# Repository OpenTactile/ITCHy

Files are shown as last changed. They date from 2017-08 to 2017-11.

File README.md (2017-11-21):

# ITCHy
The *Interactive Tactile display Control Handle*

ITCHy is a combined input/output device similar to a conventional computer mouse. It provides accurate tracking of absolute position, orientation as well as translational and angular velocities - thanks to its *two* ADNS9800 laser sensors. Using a total of 20 vibrating actuators, various tactile impressions can be transmitted to ones fingertip. Additional buttons and a RGB LED allows for basic user interaction.

ITCHy is intended to be used in conjunction with the [SCRATCHy system](https://github.com/OpenTactile/SCRATCHy).<br>
However, it can also be used in a stand-alone fashion.

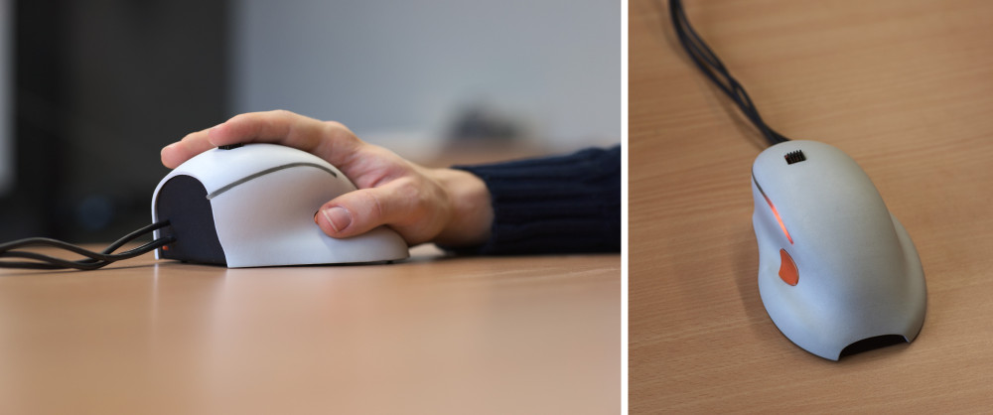
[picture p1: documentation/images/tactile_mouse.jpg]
Image of the tactile mouse


### Parts needed for building the Tactile Mouse

Positional und rotational tracking is done using two *ADSN9800 Motion Sensor* boards, both connected to a *PJRC Teensy 3.2* USB Development Board via [SPI](https://en.wikipedia.org/wiki/Serial_Peripheral_Interface_Bus). By adding some buttons and a RGB LED (optional), additional user interaction is possible.

  * Teensy 3.2 USB Development Board<br>
    see, e.g. https://www.pjrc.com/store/teensy32.html    
  * Two ADNS 9800 Laser Motion Sensors<br>
    https://www.tindie.com/products/jkicklighter/adns-9800-laser-motion-sensor/
  * Flexible USB-A to Micro-USB cable of appropriate length  
  * Microswitch (as used in computer mice, e.g. [this one](http://www.newark.com/omron-electronic-components/d2f/microswitch-pin-plunger-spdt-3a/dp/36K7257)) for the thumb button
  * Tactile switch for the reset button (e.g. [this one](http://www.newark.com/alps/skhhaqa010/switch-tactile-6x6mm-vert-red/dp/94T3234))
  * (optional) RGB LED or 3 individual LEDs
  * (optional) Appropriate resistors for operating the LEDs
  
3D printable parts are located in the *tactileMouse* subfolder. For convenience, single parts have been exported to *stl* Format that should be appropriate for most manufacturers. If modifications are needed, please use [Blender](https://www.blender.org/) for editing the *tactileMouse.blend* file.

We have positive experiences with [Shapeways](https://www.shapeways.com/) for manufacturing the parts using the following materials:

  * mouse_base.stl &rarr; [Strong & Flexible Plastic](https://www.shapeways.com/materials/strong-and-flexible-plastic), Black
  * mouse_buttons.stl &rarr; [Strong & Flexible Plastic](https://www.shapeways.com/materials/strong-and-flexible-plastic), Orange Polished
  * mouse_cover.stl &rarr; [Strong & Flexible Plastic](https://www.shapeways.com/materials/strong-and-flexible-plastic), White Polished
  * mouse_diffusor.stl &rarr; [Acrylic Plastic](https://www.shapeways.com/materials/acrylic-plastic), Transparent Acrylic (Transparent Detail)

***Important: Always check dimensions of individual parts before printing!***

### Parts needed for building the tactile display

Similar to the Tactile Mouse, parts for 3D printing the tactile display are located in the folder *tactileDisplay*. Depending on the PZT actuators to be used, modifications may have to be done to the "spacer" part within the *tactileDisplay.blend* file.

If the parts are printed using Shapeways, the following materials are appropriate:

  * base.stl &rarr; [Strong & Flexible Plastic](https://www.shapeways.com/materials/strong-and-flexible-plastic), e.g. Blue Polished
  * holder.stl (optional part, not needed for operation)
  * press_merged.stl &rarr; [Steel](https://www.shapeways.com/materials/steel), e.g. Polished Nickel<br>
    To save money, both halves of the press have been merged into a single part. Please separate (and clean) the parts manually.
  * spacer.stl &rarr; [Frosted Ultra Detail](https://www.shapeways.com/materials/frosted-detail-plastic)<br>
    *Be careful, the small springs are extremely brittle!*
  * top.stl &rarr; [Strong & Flexible Plastic](https://www.shapeways.com/materials/strong-and-flexible-plastic), e.g. White Polished
  
Additional parts needed:
  * 4x Cylinderhead screw, M2.5 x 30mm
  * 4x M2.5 nut
  * Cable for connecting the actuators<br>(depending of the chosen actuator configuration, choose as flexible and light as possible)

Please have a look into the *tactileDisplay.blend* file to get an idea on how to put the parts together.

**Hint:** Applying some electrical isolation (e.g. some layers of enamel) on the top of the actuators is generally a good idea. Otherwise the driving voltage may come into direct contact with the fingertip!

This is how it should look like after assembling the parts:
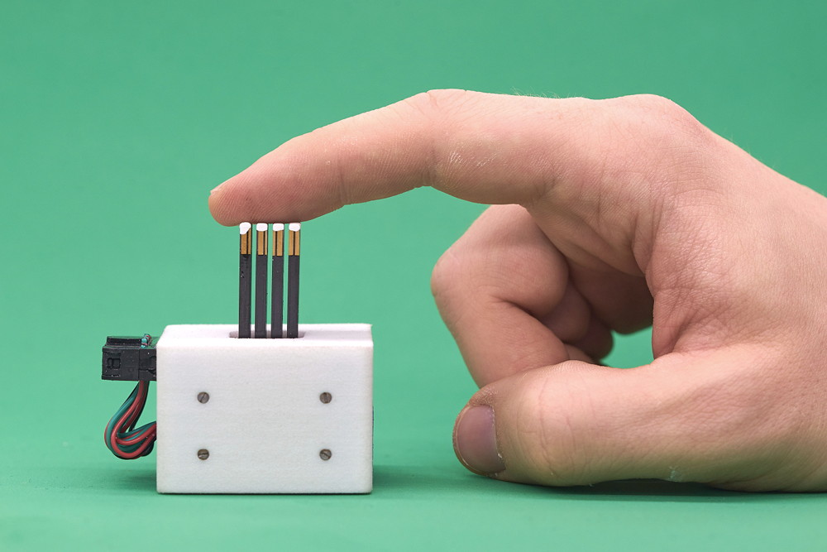
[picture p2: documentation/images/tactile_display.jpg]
Image of the tactile display


### Building libITCHy
libITCHy uses the qmake build system and is available for linux platforms only. For building and installing the library system-wide, please follow these steps within the base directory:

```shell
mkdir libITCHy-build
cd libITCHy-build
qmake ../libITCHy
make && make install
```

### Building and flashing the firmware
Before the Teensy can be flashed, please install Teensyduino by following the [official instructions](https://www.pjrc.com/teensy/td_download.html). Afterwards, building and flashing the firmware is straightforward:

```shell
cd teensyHIDSimulator
make
```
If the build process was successfull, you can install the firmware by connecting the Teensy (or better say the whole Tactile Mouse) via USB and running

```shell
make upload
```
Afterwards, the RGB LED of the mouse should blink shortly in a orangish color after connecting it to USB.

### Calibrating and testing the sensors
After libITCHy has been installed, the sensors can be tested using the *ITCHyCalibration* application:

```shell
mkdir ITCHyCalibration-build
cd ITCHyCalibration-build
qmake ../ITCHyCalibration
make
./ITCHyCalibration
```

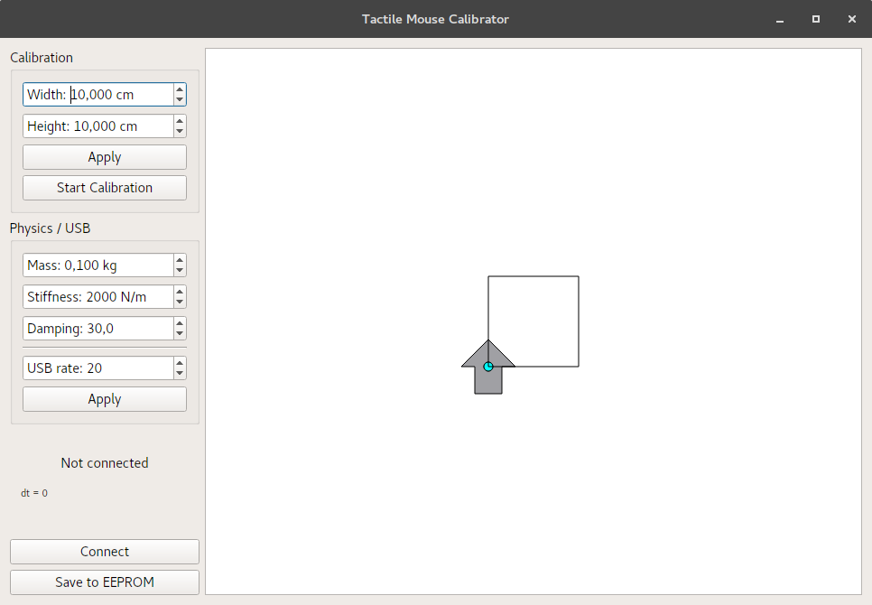
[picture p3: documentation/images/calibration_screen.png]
The calibration application


After connecting the tactile mouse and by pressing the *Connect* button, the status area on the left should show "Connected" and the current simulation timestep should be displayed.

##### Calibration procedure
When connecting the tactile mouse for the first time, a calibration of the sensors is needed. Please follow this procedure for proper calibration:
1. Use a (probably quite large) hard-plastic mousepad
2. Mark a distance of e.g. 10cm (or larger depending on the dimensions of the mousepad) in horizontal direction as well as in vertical direction
3. Register these distance within the GUI and click *Apply*
4. Place the tactile mouse in the bottom left of the calibration area
5. Click *Start Calibration*
6. Steadily move the device across the horizontal marker
7. Press the thumb button
8. Steadily move the device across the vertical marker
9. Press the thumb button again

After this procedure is finished, moving the mouse should show a corresponding reaction of the "arrow" in the window. You can reset orientation and position to defaults at any time by pressing the small button at the front of the device.

The ADNS sensors seem to be quite picky regarding the surface properties of the mousepad. In case no proper calibration is possible, please try another one. We made good experiences with the [Corsair MM400](http://www.corsair.com/en-ww/mm400-high-speed-gaming-mouse-pad) mousepad.

In order to save the new calibration data permanently, press the *Save to EEPROM* button.

##### Parameter tuning
The firmware inside the tactile mouse use a simple physics simulation that models the virtual representation of itself as a rigid body attached to the actual sensor position via two springs. The parameters shown in the GUI allow to adjust the simulation parameters such as:
- The mass of the rigid body,
- the stiffness of the springs and
- a damping factor for suppressing oscillations

After changing the values and hitting *Apply* the changes are visible immediately. Again, they will be store permanently after the *Save to EEPROM* button has been pressed.

By adjusting the *USB rate* of the tactile mouse, one can limit the polling rate of the device. This value can be decreased down to 1ms, resulting in a maximum polling rate of 1000Hz. Please note, however, that this may increase the load of the host system (and the kernel actually has to support such high polling rates).

### Using libITCHy
Using libITCHy directly (without SCRATCHy) is straightforward, as can be seen in this minimal example program:
```cpp
#include <itchy.h>
#include <cmath>

int main(int argc, char *argv[]) {
    ITCHy mouse;
    mouse.connect(); // Wait until the mouse gets connected
    
    // This variable will hold the last valid state
    // e.g. velocity, position, etc.
    ITCHy::State state = mouse.currentState(); 

    while(state.button == 0) { // Loop until a button on the mouse gets pressed
        state = mouse.currentState(); // Update state via USB
        
        // Change the internal RGB LED
        mouse.setColor({uint8_t(255 * 10 * state.velocity[0]),
                        uint8_t(255 * 10 * state.velocity[1]),
                        uint8_t(255 * state.angle / (2 * M_PI))});
    }

    mouse.disconnect();
    return 0;
}
```
This example program should be pretty self-explanatory.
Compiling and running this application can be done as follows:
```shell
g++ -o itchyMinimal minimal.cpp -I/usr/include/itchy/ -lITCHy
./itchyMinimal
```
When moving the tactile mouse, the RGB LED now should change colors according to the current speed and orientation of the device.

### Using the Python bindings
If you prefer to access the Tactile Mouse using Python, the ITCHPy library can be build as follows:

```shell
cd ITCHPy
make
```

To test if all dependencies are met and the whole build process was successful run
```shell
python itchpytest.py
```
within the same directory.

This file also gives some hints on how to include ITCHPy in your projects.

## API Reference

#### ICTHy
This class allows to communicate with the hardware device directly (without the need for libSCRATCHy).

The default constructor assumes that the Teensy 3.2 that is used within the mouse can be identified using the ID `{0x16C0, 0x0486, 0xFFAB, 0x0200}`. 
In case this default has been changed, the ID to connect to can be specified manually by calling `ITCHy({0x????, 0x????, 0x????, 0x????})`

##### `void connect()`
Tries to connect to the device via USB periodically. Will return after ITCHy has been successfully initialized. (Blocking operation)

After successfull initialization, the `Connected` callback will be executed.

##### `bool tryConnect()`
Tries to connect to the device via USB *once*. Returns `true` if the devices has been initialized successfully or `false` if the device has not been found.

After successfull initialization, the `Connected` callback will be executed.

##### `void disconnect()`
Closes the USB device handle and executes the `Disconnected` callback afterwards.

##### `bool connected() const`
Returns whether the USB devices has been successfully initialized or not.

##### `bool setCalibrationParameters(const vec2f& target)`
Sets the dimensions of the calibration area in metres. Using the *ITCHyCalibration* application is the recommended way to alter this value.

Returns `false` if the device is not connected or a USB communication error occured.

##### `bool setSimulationParameters(float mass, float stiffness, float damping, int updateRate)`
Sets the internal simulation parameters of the tactile mouse and causes these values to be used immediately.

In case instabilities occur due to wrong parameters, a total reset of the device is needed!
Using the *ITCHyCalibration* application is the recommended way to alter this value.

Returns `false` if the device is not connected or a USB communication error occured.

##### `bool setColor(const color& cl)`
Changes the color of the built in RGB LED. Color values are specified within 0...255 range. 

For example
```cpp
setColor({255, 128, 0})
```
will cause the LED to emit an orange color, while
```cpp
setColor({0, 0, 0})
```
will turn off the LED.

Returns `false` if the device is not connected or a USB communication error occured.

##### `bool startCalibration()`
Initiates the calibration process as has been discussed in section *Calibration procedure*.

Returns `false` if the device is not connected or a USB communication error occured.

##### `bool saveState()`
Stores the current configuration to the internal EEPROM, causing these settings to be loaded automatically after connecting.

This method will store the following data:

- Size of calibration area
- Calibration matrix for both sensors
- Simulation parameters (mass, stiffness, damping and USB update rate)

Returns `false` if the device is not connected or a USB communication error occured.

##### `const State& currentState(unsigned int timeout = 50)`
Tries to acquire the latest state of the tactile mouse via USB, waiting a maximum of `timeout` milliseconds for the device to react. In case no new data is available or a timeout occured, the last valid state will be returned. 

The returned struct should be self-explanatory:
```cpp
struct State {
  // Actual output (25 bytes)
  vec2f position;
  float angle;
  vec2f velocity;
  float angularVelocity;
  byte  button;

  // Raw sensor data (16 bytes)
  vec2f leftSensor; // equals std::array<float, 2>
  vec2f rightSensor; // equals std::array<float, 2>

  // Debug data (8 bytes)
  vec2s leftIncrement;    // Contains sensor delta since last USB frame, equals std::array<int16_t, 2>
  vec2s rightIncrement;   // Contains sensor delta since last USB frame, equals std::array<int16_t, 2>

  // Simulation info (8 bytes)
  float timeStep;
  float time;

  // Unused
  byte unused[7];
};
```
In case a USB communication error occured, the device will be disconnected and the `CommunicationError` callback will be executed.

##### `void addCallback(CallbackType type, const std::function<void()>& callback)`
Allows to register a custom function that will be called if the corresponsing event happens. 

Multiple functions can be added. However, removing them afterwards is currently not supported.

The following example will print an error message in case USB communication failed:
```cpp
  itchyinstance.addCallback(
    ITCHy::CallbackType::CommunicationError, 
    [](){ // Add lambda function
      std:cout << "USB error" << std::endl;
    });
```

#### TactileMouseQuery
This class implements the `PositionQuery` defined in libSCRATCHy. Please refer to the [interface documentation](https://github.com/OpenTactile/SCRATCHy#positionquery) for further details.
ITCHy supports all of the `PositionQuery` calls, such as retrieval of position, orientation, velocity, angular velocity and status of the thumb button. Using the `feedback` method, the colour of the integrated LED can be changed freely.

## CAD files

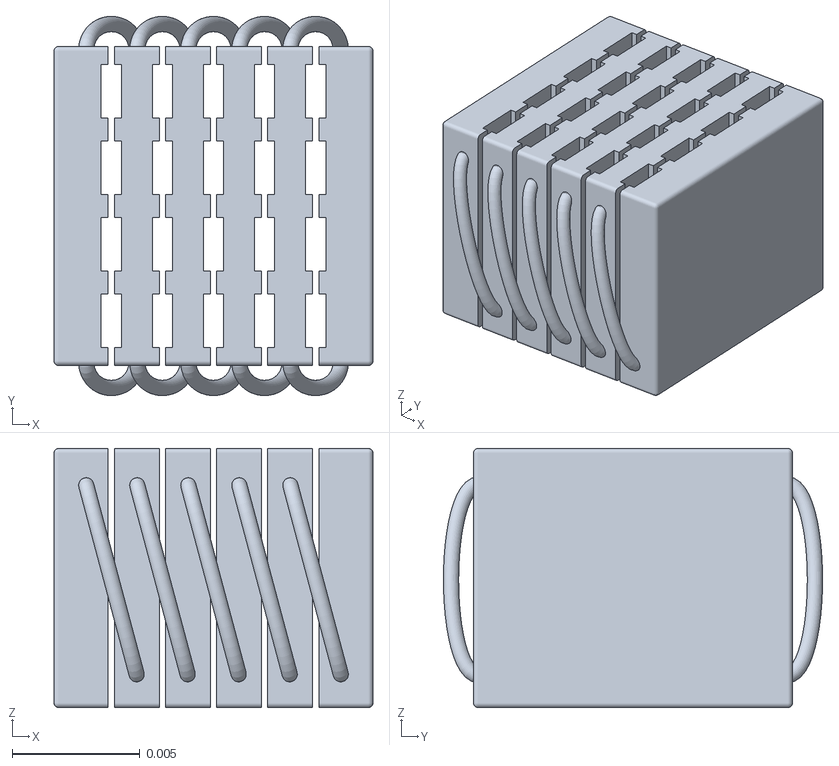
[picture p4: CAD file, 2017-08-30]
tactileDisplay/parts/spacer.stl
0.0125 x 0.0149 x 0.0101

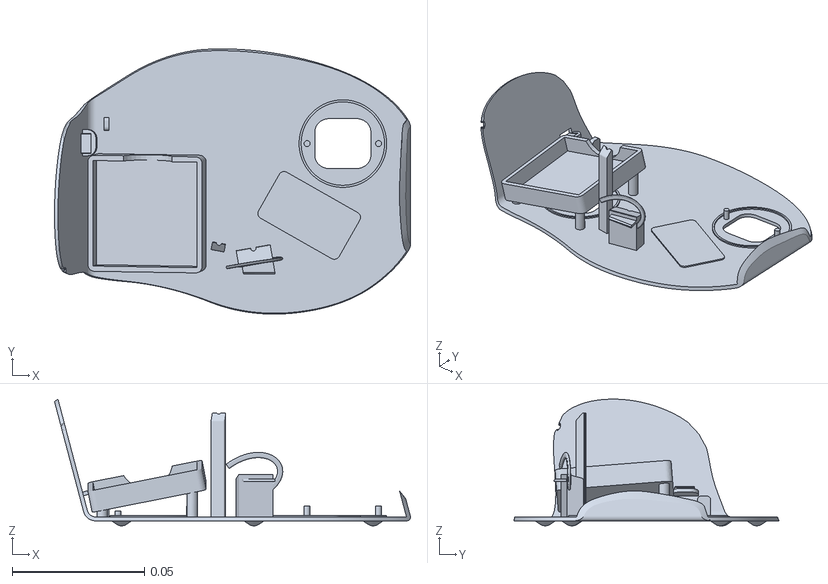
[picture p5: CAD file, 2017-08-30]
tactileMouse/parts/mouse_base.stl
0.134 x 0.1 x 0.0479

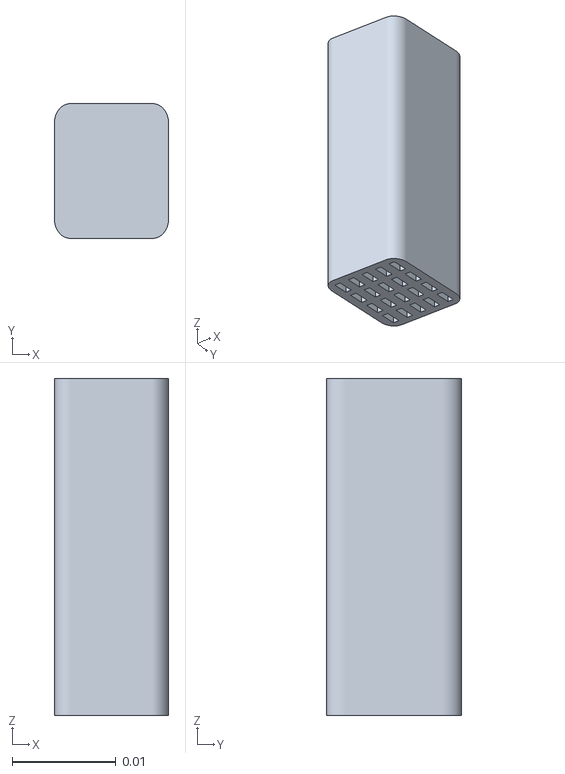
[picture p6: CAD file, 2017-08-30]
tactileDisplay/parts/holder.stl
0.011 x 0.013 x 0.0325

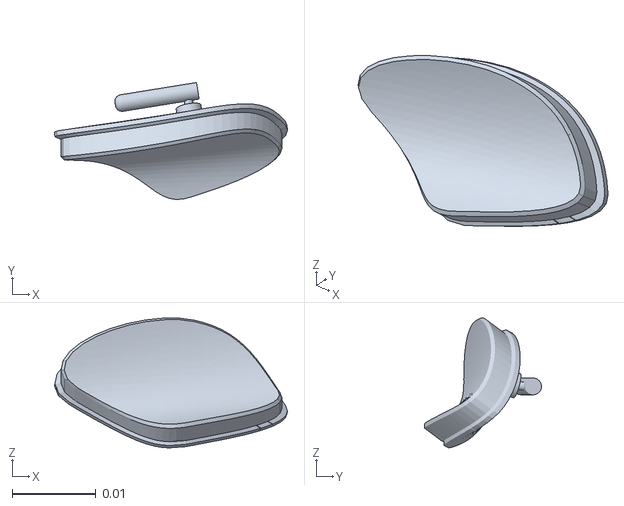
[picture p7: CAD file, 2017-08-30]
tactileMouse/parts/mouse_buttons.stl
0.0278 x 0.014 x 0.0155

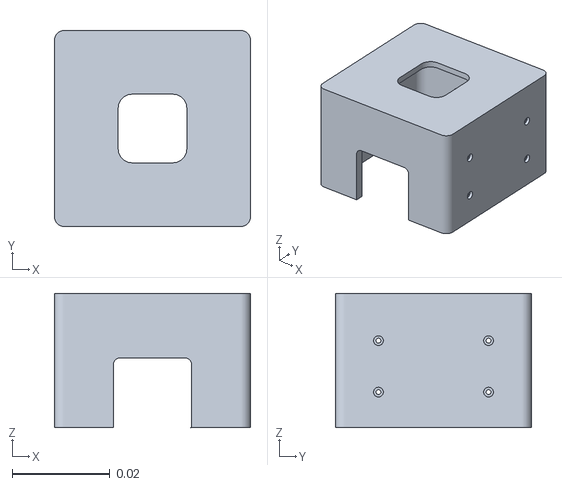
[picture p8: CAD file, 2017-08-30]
tactileDisplay/parts/top.stl
0.04 x 0.04 x 0.0274

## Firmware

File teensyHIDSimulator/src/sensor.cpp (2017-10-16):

#include "sensor.h"

#include <WProgram.h>
#include <avr/pgmspace.h>
#include "../firmware/adns9800_srom_A6.h"
#include "statusled.h"
#include <SPI.h>

// Registers
#define REG_Product_ID                           0x00
#define REG_Revision_ID                          0x01
#define REG_Motion                               0x02
#define REG_Delta_X_L                            0x03
#define REG_Delta_X_H                            0x04
#define REG_Delta_Y_L                            0x05
#define REG_Delta_Y_H                            0x06
#define REG_SQUAL                                0x07
#define REG_Pixel_Sum                            0x08
#define REG_Maximum_Pixel                        0x09
#define REG_Minimum_Pixel                        0x0a
#define REG_Shutter_Lower                        0x0b
#define REG_Shutter_Upper                        0x0c
#define REG_Frame_Period_Lower                   0x0d
#define REG_Frame_Period_Upper                   0x0e
#define REG_Configuration_I                      0x0f
#define REG_Configuration_II                     0x10
#define REG_Frame_Capture                        0x12
#define REG_SROM_Enable                          0x13
#define REG_Run_Downshift                        0x14
#define REG_Rest1_Rate                           0x15
#define REG_Rest1_Downshift                      0x16
#define REG_Rest2_Rate                           0x17
#define REG_Rest2_Downshift                      0x18
#define REG_Rest3_Rate                           0x19
#define REG_Frame_Period_Max_Bound_Lower         0x1a
#define REG_Frame_Period_Max_Bound_Upper         0x1b
#define REG_Frame_Period_Min_Bound_Lower         0x1c
#define REG_Frame_Period_Min_Bound_Upper         0x1d
#define REG_Shutter_Max_Bound_Lower              0x1e
#define REG_Shutter_Max_Bound_Upper              0x1f
#define REG_LASER_CTRL0                          0x20
#define REG_Observation                          0x24
#define REG_Data_Out_Lower                       0x25
#define REG_Data_Out_Upper                       0x26
#define REG_SROM_ID                              0x2a
#define REG_Lift_Detection_Thr                   0x2e
#define REG_Configuration_V                      0x2f
#define REG_Configuration_IV                     0x39
#define REG_Power_Up_Reset                       0x3a
#define REG_Shutdown                             0x3b
#define REG_Inverse_Product_ID                   0x3f
#define REG_Motion_Burst                         0x50
#define REG_SROM_Load_Burst                      0x62
#define REG_Pixel_Burst                          0x64

Sensor::Sensor(std::array<unsigned char, 2> pins, bool flipX, bool flipY)
{
    this->lifted = false;
    this->flipX = flipX;
    this->flipY = flipY;
    integrated = {{0,0}};
    this->pins = pins;
    pinMode (pins[0], OUTPUT); // Chip select
    pinMode (pins[1], INPUT_PULLUP); // Motion pin
    //attachInterrupt(mot, sensorChanged, FALLING);

    // TODO: which parts of the code have to be executed once / foreach sensor ?
    adns_com_end(); // ensure that the serial port is reset
    adns_com_begin(); // ensure that the serial port is reset
    adns_com_end(); // ensure that the serial port is reset
    adns_write_reg(REG_Power_Up_Reset, 0x5a); // force reset
    delay(50); // wait for it to reboot
    // read registers 0x02 to 0x06 (and discard the data)
    adns_read_reg(REG_Motion);
    adns_read_reg(REG_Delta_X_L);
    adns_read_reg(REG_Delta_X_H);
    adns_read_reg(REG_Delta_Y_L);
    adns_read_reg(REG_Delta_Y_H);
    // upload the firmware
    uploadFirmware();

    delay(10);
    //enable laser(bit 0 = 0b), in normal mode (bits 3,2,1 = 000b)
    // reading the actual value of the register is important because the real
    // default value is different from what is said in the datasheet, and if you
    // change the reserved bytes (like by writing 0x00...) it would not work.
    byte laser_ctrl0 = adns_read_reg(REG_LASER_CTRL0);
    adns_write_reg(REG_LASER_CTRL0, laser_ctrl0 & 0xf0 );
    //adns_write_reg(REG_Configuration_I, 0x01 ); // 200 dpi
    //adns_write_reg(REG_Configuration_I, 0x09 ); // 1800 dpi
    //adns_write_reg(REG_Configuration_I, 0x29 ); // 8200 dpi
    adns_write_reg(REG_Configuration_I, 0xA4 ); // 8200 dpi

    delay(1);
}

void Sensor::setCalibrationTarget(vec2f target)
{
    calibrationTarget = target;
}

void Sensor::adns_com_begin()
{
    digitalWrite(pins[0], LOW);
}

void Sensor::adns_com_end()
{
    digitalWrite(pins[0], HIGH);
}

byte Sensor::adns_read_reg(byte reg_addr)
{
    adns_com_begin();    
    SPI.transfer(reg_addr & 0x7f );
    delayMicroseconds(100);
    byte data = SPI.transfer(0);
    delayMicroseconds(1);
    adns_com_end();
    delayMicroseconds(19);
    return data;
}

void Sensor::adns_write_reg(byte reg_addr, byte data)
{
    adns_com_begin();    
    SPI.transfer(reg_addr | 0x80 );
    SPI.transfer(data);
    delayMicroseconds(20);
    adns_com_end();
    delayMicroseconds(100);
}

void Sensor::uploadFirmware()
{    
    adns_write_reg(REG_Configuration_IV, 0x02);
    adns_write_reg(REG_SROM_Enable, 0x1d);
    delay(10);
    adns_write_reg(REG_SROM_Enable, 0x18);
    adns_com_begin();
    SPI.transfer(REG_SROM_Load_Burst | 0x80);
    delayMicroseconds(15);
    unsigned char c;
    for (int i = 0; i < firmware_length; i++) {
      c = (unsigned char)pgm_read_byte(firmware_data + i);
      SPI.transfer(c);
      delayMicroseconds(15);
    }
    adns_com_end();
}

vec2f Sensor::integrate()
{
    vec2f delta = {{0.0f, 0.0f}};
    short deltaX = 0;
    short deltaY = 0;

    byte motion = adns_read_reg(REG_Motion);

    // semantic see datasheet
    bool motionOccured = motion & 0x80;
    bool motionFault = motion & 0x40;
    bool laserValid = motion & 0x20;

    byte SQUAL = adns_read_reg(REG_SQUAL);
    lifted = (SQUAL < 50);

    if(motionOccured && !motionFault && laserValid)
    {
        deltaX = (short) adns_read_reg(REG_Delta_X_L) |
                    ((short) adns_read_reg(REG_Delta_X_H) << 8);
        deltaY = (short) adns_read_reg(REG_Delta_Y_L) |
                    ((short) adns_read_reg(REG_Delta_Y_H) << 8);
    }

    if(!laserValid)
    {
        StatusLED::instance().blink({{255,0,0}}, 1.0);
        StatusLED::instance().blink({{255,128,0}}, 0.5);
    }

    if(motionFault)
    {
        StatusLED::instance().blink({{255,0,0}}, 1.0);
        StatusLED::instance().blink({{255,128,0}}, 0.5);
        StatusLED::instance().blink({{255,128,0}}, 0.5);
    }

    if(flipX)
        deltaX *= -1;
    if(flipY)
        deltaY *= -1;

    integrated[0] += deltaX;
    integrated[1] += deltaY;

    delta[0] = deltaX;
    delta[1] = deltaY;

    delta[0] *= calib.scale[0];
    delta[1] *= calib.scale[1];

    delta = mul(correction, delta);
    return delta;
}

vec2f Sensor::absolutePosition()
{
    vec2f pos = {{
                     integrated[0] * calib.scale[0],
                     integrated[1] * calib.scale[1]
                 }};    
    //return pos;
    return mul(correction, pos);
}

void Sensor::reset()
{
    integrated[0] = 0;
    integrated[1] = 0;

    // Delete previous sensor data
    adns_read_reg(REG_Motion);
    adns_read_reg(REG_Delta_X_L);
    adns_read_reg(REG_Delta_X_H);
    adns_read_reg(REG_Delta_Y_L);
    adns_read_reg(REG_Delta_Y_H);

    //adns_write_reg(REG_Motion, 0);
}

void Sensor::calibrationStart()
{
    StatusLED::instance().blink({255,64,0}, 0.5);
    reset();
}

Sensor::CalibrationState Sensor::calibration()
{
    return calib;
}

bool Sensor::isLifted() const
{
    return lifted;
}

void Sensor::setCalibration(const Sensor::CalibrationState& cal)
{
    calib = cal;

    correctionAlpha = acos(calib.alpha[0]);

    correction = {{
                     calib.alpha[0], calib.alpha[1],
                    -calib.alpha[1],  calib.alpha[0]
                  }};

    reset();
}

void Sensor::calibrationFinishX()
{    

    vec2f target = {{1.0,0.0}};
    vec2f measured = normalized({{
                              float(integrated[0]),
                              float(integrated[1])
                          }});

    calib.alpha[0] = dot(target, measured);
    calib.alpha[1] = cross(target, measured);

    correctionAlpha = acos(calib.alpha[0]);

    correction = {{
                     calib.alpha[0], calib.alpha[1],
                    -calib.alpha[1],  calib.alpha[0]
                  }};

    float dxLen = correction[0] * calibrationTarget[0]/len(integrated);

    //float dxLen = calibrationTarget[0]/integrated[0];
    calib.scale[0] = dxLen;

    reset();
}


void Sensor::calibrationFinishY()
{
    float dyLen = correction[0] * calibrationTarget[1]/len(integrated);
    //float dyLen = calibrationTarget[1]/integrated[1];
    calib.scale[1] = dyLen;

    reset();
}

float Sensor::correctionAngle() const
{
    return correctionAlpha;
}

vec2l Sensor::rawPosition()
{
    return integrated;
}

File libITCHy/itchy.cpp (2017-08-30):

#include "itchy/itchy.h"

extern "C" {
#include "pjrc_rawhid.h"
}

#include <unistd.h>
#include <vector>
#include <map>

template<typename T>
unsigned int typeToBuffer(char* buffer,const T& type, unsigned int start=0, unsigned int typeLength=1) {
    char* p = (char *)((void *)(&type));
    buffer += start;
    unsigned int typeSize = sizeof(T)*typeLength;
    unsigned int i;
    for(i=0; i<typeSize; i++) {
        *buffer++ = *p++;
    }
    return i;
}

template<typename T>
unsigned int bufferToType(const char* buffer, T& type, unsigned int start=0, unsigned int typeLength=1) {
    char* p = (char *)((void *)(&type));
    buffer += start;
    unsigned int typeSize = sizeof(T)*typeLength;
    unsigned int i;
    for(i=0; i<typeSize; i++) {
        *p++ = *buffer++;
    }
    return i;
}

class ITCHyImplementation
{
public:

    enum USBOpCodes
    {
        Invalid = 0,
        CalibrationData = 1,
        SimulationData = 2,
        SetColor = 3,
        SaveConfig = 4,
        Calibrate = 5
    };

    DeviceIdentifier identifier;
    bool connected = false;

    std::map<ITCHy::CallbackType,
             std::vector<std::function<void()>>> callbacks;

    void callAll(ITCHy::CallbackType type)
    {
        for(auto& fun : callbacks[type])
        {
            fun();
        }
    }

    ITCHy::State lastState;
};

ITCHy::ITCHy() :
    ITCHy({0x16C0, 0x0486, 0xFFAB, 0x0200})
{
}

ITCHy::ITCHy(DeviceIdentifier identifier)
{
    impl = new ITCHyImplementation();

    impl->identifier = identifier;
    impl->lastState.leftSensor = {{0.0, 0.0}};
    impl->lastState.rightSensor = {{0.0, 0.0}};
}

ITCHy::~ITCHy()
{
    delete impl;
}

void ITCHy::connect()
{
    while(!tryConnect())
    {
        usleep(10000);
    }
}

bool ITCHy::tryConnect()
{
    if(impl->connected)
    {
        return true;
    }

    int ret = rawhid_open(1,
                          impl->identifier[0], impl->identifier[1],
                          impl->identifier[2], impl->identifier[3]);

    // Device not found
    if(ret <= 0)
    {
        return false;
    }

    // Device found
    impl->connected = true;
    impl->callAll(CallbackType::Connected);
    return true;
}

void ITCHy::disconnect()
{
    if(impl->connected)
    {
        rawhid_close(0);
        impl->connected = false;
        impl->callAll(CallbackType::Disconnected);
    }
}

bool ITCHy::connected() const
{
    return impl->connected;
}

bool ITCHy::setCalibrationParameters(const vec2f& target)
{
    if(!impl->connected)
    {
        return false;
    }

    char buffer[64] = {0};
    int p = 0;
    char opcode = ITCHyImplementation::CalibrationData;
    p += typeToBuffer(buffer, opcode, p);
    p += typeToBuffer(buffer, target[0], p, 2);

    int ret = rawhid_send(0, buffer, 64, 1000);

    if(ret <= 0)
    {
        impl->callAll(CallbackType::CommunicationError);
        return false;
    }

    return true;
}

bool ITCHy::setSimulationParameters(
        float mass,
        float stiffness,
        float damping,
        int updateRate
        )
{
    if(!impl->connected)
    {
        return false;
    }

    char buffer[64] = {0};
    int p = 0;
    char opcode = ITCHyImplementation::SimulationData;
    p += typeToBuffer(buffer, opcode, p);
    p += typeToBuffer(buffer, damping, p);
    p += typeToBuffer(buffer, mass, p);
    p += typeToBuffer(buffer, stiffness, p);
    p += typeToBuffer(buffer, updateRate, p);

    int ret = rawhid_send(0, buffer, 64, 1000);

    if(ret <= 0)
    {
        impl->callAll(CallbackType::CommunicationError);
        return false;
    }

    return true;
}

bool ITCHy::setColor(const color& cl)
{
    if(!impl->connected)
    {
        return false;
    }

    char buffer[64] = {0};
    int p = 0;
    char opcode = ITCHyImplementation::SetColor;
    p += typeToBuffer(buffer, opcode, p);
    p += typeToBuffer(buffer, cl[0], p, 3);

    int ret = rawhid_send(0, buffer, 64, 50);

    if(ret <= 0)
    {
        impl->callAll(CallbackType::CommunicationError);
        return false;
    }

    return true;
}

bool ITCHy::startCalibration()
{
    if(!impl->connected)
    {
        return false;
    }

    char buffer[64] = {0};
    int p = 0;
    char opcode = ITCHyImplementation::Calibrate;
    p += typeToBuffer(buffer, opcode, p);

    int ret = rawhid_send(0, buffer, 64, 1000);


    if(ret <= 0)
    {
        impl->callAll(CallbackType::CommunicationError);
        return false;
    }

    return true;
}

bool ITCHy::saveState()
{
    if(!impl->connected)
    {
        return false;
    }

    char buffer[64] = {0};
    int p = 0;
    char opcode = ITCHyImplementation::SaveConfig;
    p += typeToBuffer(buffer, opcode, p);

    int ret = rawhid_send(0, buffer, 64, 1000);


    if(ret <= 0)
    {
        impl->callAll(CallbackType::CommunicationError);
        return false;
    }

    return true;
}

const ITCHy::State& ITCHy::currentState(unsigned int timeout)
{
    if(!impl->connected)
    {
        return impl->lastState;
    }

    union
    {
        State newState;
        char buffer[64];
    } data;

    // USB Read
    int num = rawhid_recv(0, data.buffer, 64, static_cast<int>(timeout));

    // Error
    if(num < 0)
    {
        impl->callAll(CallbackType::CommunicationError);
        disconnect();
    }
    else
    {
        State newState = data.newState;
        impl->lastState = newState;
    }

    return impl->lastState;
}


void ITCHy::addCallback(
        CallbackType type, const std::function<void()>& callback)
{
    impl->callbacks[type].push_back(callback);
}

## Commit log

2017-08-30 Add simple calibration GUI for ITCHy
2017-08-30 Add Teensy HID Simulator
2017-08-30 Add tactileMouse mesh
    [mouse_base.stl, mouse_buttons.stl]
2017-08-30 Add tactileDisplay parts and blend file
    [holder.stl, spacer.stl, top.stl]
